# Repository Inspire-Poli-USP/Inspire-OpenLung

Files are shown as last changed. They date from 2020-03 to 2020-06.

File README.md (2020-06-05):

# Inspire-OpenLung

<p align="center">
<a href="https://github.com/Inspire-Poli-USP/Inspire-OpenLung/blob/master/LICENSE" alt="License CERN Open Hardware V2">
        </a>

<a href="https://t.me/openlungpoliusp" alt="Chat em grupo no Telegram">
        </a>

<a href="https://groups.google.com/forum/#!forum/inspireopenlung" alt="Lista de email">
        </a>

<a href="https://inspire-poli-usp.github.io/Inspire-OpenLung/" alt="Docs website">
        </a>
</p>

Seja muito bem vindo ao repositório do projeto de hardware livre OpenLung! Um respirador emergencial brasileiro para enfrentamento da COVID-19!

Um projeto da iniciativa [Inspire Poli-USP](https://www.poli.usp.br/inspire), uma de oito iniciativas da Universidade de São Paulo envolvendo viabilização de respiradores para enfrentamento à pandemia. Para saber mais sobre essa e outras iniciativas [veja esse link](https://prp.usp.br/usp-e-covid-19/).

Considere também apoiar o financiamento de pesquisas na USP para o combate à COVID-19 [através do programa USP Vida](https://www5.usp.br/uspvida/).

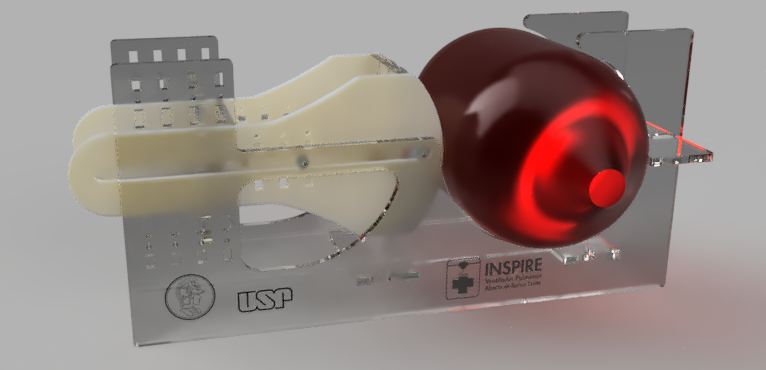
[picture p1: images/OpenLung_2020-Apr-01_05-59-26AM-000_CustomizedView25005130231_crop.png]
Model of CITI-OpenLung


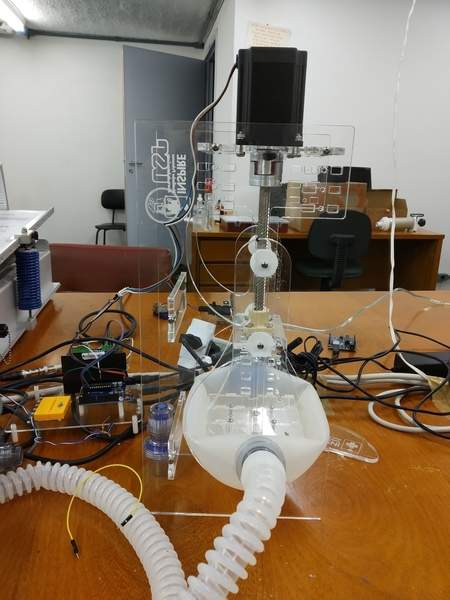
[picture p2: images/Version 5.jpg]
Photo of Prototype Version 5 (https://youtu.be/7Tz8H8FaeOk)


(Clique na imagem acima para ver um vídeo do protótipo em ação)

* * *

## :warning: ATENÇÃO :warning:

-   **Este é um projeto em andamento, não é um produto pronto.**
-   **O projeto em seu atual estado NÃO DEVE SER USADO EM HUMANOS.**
-   **O projeto em seu estado atual NÃO DEVE SER USADO EM ANIMAIS sem aprovação de comitês de ética legítimos.**
-   **Caso futuramente aprovado por autoridades competentes, o projeto NÃO DEVE SER FABRICADO E DISTRIBUÍDO SEM OS CONTROLES DE QUALIDADE necessários para seu uso.**
-   **As entidades e pessoas envolvidas no desenvolvimento desse projeto NÃO SE RESPONSABILIZAM pelo uso de má fé das informações deste projeto ou de projetos derivados deste, que possam por exemplo, mas não limitando-se a, ferir, prejudicar, ludibriar, adoecer, contaminar ou lesar quaisquer pessoas. Caso você julgue ter observado o mau uso deste projeto em quaisquer circunstâncias, nos informe imediatamente pelo contato [inspire@usp.br](mailto:inspire@usp.br) . Sua colaboração é importante para a segurança deste projeto.**
-   **Este projeto usa a licença [CERN-OHL-S 2.0](https://github.com/emersonmoretto/CITI-OpenLung/blob/master/LICENSE).**

* * *

## :exclamation: ATUALIZAÇÃO IMPORTANTE :exclamation:

Devido a questões jurídicas, o entendimento dos coordenadores do projeto é de que o software que realiza o controle do Ambu, bem como os dados experimentais associados aos testes dos algoritmos de controle, permanecerão **privados** até o término dos testes.

Lamentamos essas medidas e estamos discutindo a **possibilidade** do compartilhamento restrito dessas informações com grupos de contribuidores especiais (como centros de pesquisa, universidades, empresas etc) interessados em contribuir com o projeto. Mas isso ainda não está decidido.

Existem [outros repositórios](https://github.com/Inspire-Poli-USP/Inspire-OpenLung/wiki/Outros-Projetos) **independentes da iniciativa Inspire** que estão desenvolvendo, disponibilizando ou prometem disponibilização de firmwares, como por exemplo o [OdaMV](https://github.com/eduoda/odamv), o [ReesistenciaTeam](https://gitlab.com/reesistencia/reespirator/-/tree/dev/rees_firmware), o [hitecnologia/cov19](https://github.com/hitecnologia/cov19) ou o [BMV OpenLung](https://gitlab.com/open-source-ventilator/ventilator/OpenLung/-/tree/master/) - bem como [essa lista de projetos](https://soptechint.com/ventilators). Contudo não nos responsabilizamos pelo uso destes firmwares com nosso hardware e reforçamos a atenção para os [importantes avisos no início desta página](#warning-atenção-warning).

Caso tenha alguma dúvida, pedido ou reclamação, entre em contato com [inspire@usp.br](mailto:inspire@usp.br).

Vale notar que, desde o dia 14 de Abril, o projeto não recebe atualizações em relação ao respirador. Portanto, o que se encontra nesse repositório é tudo que foi feito até essa data e não incorre em problemas jurídicos para equipe do Inspire. Você pode acompanhar as últimas atualizações através dos [Vídeos Relatórios](https://github.com/Inspire-Poli-USP/Inspire-OpenLung/blob/master/LICENSE) e das [Aparições na mídia](https://github.com/Inspire-Poli-USP/Inspire-OpenLung/wiki/Apari%C3%A7%C3%B5es-na-m%C3%ADdia)

* * *

# Índice

| [Nossa Wiki](https://github.com/Inspire-Poli-USP/Inspire-OpenLung/wiki) | [Issues do Projeto](https://github.com/Inspire-Poli-USP/Inspire-OpenLung/issues) | [Pull-Requests](https://github.com/Inspire-Poli-USP/Inspire-OpenLung/pulls) | [Licença de Uso](https://github.com/Inspire-Poli-USP/Inspire-OpenLung/blob/master/LICENSE) |
| ----------------------------------------------------------------------- | -------------------------------------------------------------------------------- | --------------------------------------------------------------------------- | --------------------------------------------------------------------------------------------- |

1.  [Porque mais um projeto como esse?](#porque-mais-um-projeto-como-esse)
2.  [Motivação](#motivação)
3.  [Onde queremos chegar](#onde-queremos-chegar)
4.  [Questão Regulatória](#questão-regulatória)
5.  [Como colaborar](#como-colaborar)
6.  [Nossa Abordagem de Trabalho e Princícios de Design](#nossa-abordagem-de-trabalho-e-princípios-de-design)
7.  [Andamento do projeto](#andamento-do-projeto)</br>
    7.1 [Tarefas pendentes](#tarefas-pendentes)
8.  [Principais Especificações Desejadas](#principais-especificações-desejadas)
9.  [Lista de Materiais](#lista-de-materiais)</br>
    9.1 [Partes Mecânicas](#partes-mecânicas)</br>
    9.2 [Partes Eletrônicas](#partes-eletrônicas)</br>
    9.3 [Partes "Médicas"](#partes-médicas)
10. [Contato e Ajuda](#contato-e-ajuda)
11. [Doe para o projeto](#doe-para-o-projeto)
12. [Licença](#licença)

# Por que mais um projeto como esse

Este é mais um projeto de design de ventilador pulmonar de acesso aberto com o intuito de ser barato, de fácil transporte e utilizando poucos materiais, usando principalmente um Ambu como gerador de fluxo de ar.

Iniciamos este projeto porque até então haviam apenas propostas online com conteúdo parcialmente disponível, e apenas levando em consideração o contexto dos países em que tais propostas estavam/estão sendo desenvolvidas. Nosso projeto se baseia em [Princípios](https://github.com/Inspire-Poli-USP/Inspire-OpenLung/blob/master/Principios_e_abordagem.md) que colocam um peso maior na indisponibilidade de recursos e custo.

Vale notar também que o ventilador pulmonar inspire utiliza em sua maioria produtos que podem ser encontrados com realativa facilidade no mercado Brasileiro.

# Motivação

A expectativa é que teremos no Brasil um pico de casos a serem tratados pelo sistema de saúde pelo final do mês de Abril. Nesse momento a demanda por ventiladores pulmonares mecânicos será crítica, sendo uma das lamentáveis causas de morte pelo novo coronavirus devido a ausência de infraestrutura suficiente para a quantidade de número de pacientes. Estamos lutando contra o tempo para desenvolver um ventilador "open source" que possa ser fabricado antes que isso aconteça.

# Onde queremos chegar

A ideia final é reproduzir um respirador profissional para terapia intensiva. Ou seja:

-   Não é um projeto que se restringe a apenas apertar o Ambú ritmicamente,
-   É um projeto para reproduzir uma curva de variação de pressão definida pelo usuário (médico ou fisioterapeuta),
-   Não queremos fazer um respirador igualmente sofisticado aos comercialmente disponíveis,
-   É um projeto para ter o mínimo necessário para manter pessoas vivas com segurança, [numa situação emergencial](#warning-atenção-warning).

Veja a página ["Entenda o Problema"](https://github.com/Inspire-Poli-USP/Inspire-OpenLung/wiki/Entenda-o-Problema) para informações mais específicas sobre o escopo técnico deste projeto.

Onde queremos chegar com este braço open source da iniciativa Inspire é desenvolver os módulos centrais do ventilador, que identificamos como sendo:

-   o "apertador de Ambu",
-   e o algoritmo de controle.

Os demais módulos como eletrônica própria (sem usar arduino), interface operador-máquina e _packaging_ do sistema todo **por enquanto** não são open source. O firmware e softwares associados ao algoritmo de controle **serão compartilhados de maneira restrita** com contribuidores especiais, pelas razões explicitadas [aqui](#exclamation-atualização-importante-exclamation).

Contudo, você pode desenvolver esses outros módulos segundo seu próprio contexto local de logística e recursos. Uma produção deslocalizada e flexível é uma possibilidade em aberto para fabricação dos respiradores a tempo. Encorajamos possíveis colaboradores deste projeto a seguir o exemplo de forks desre repositório e desenvolverem suas próprias soluções complementares ao que estamos fazendo.

# Questão regulatória

Uma questão em aberto para todos os projetos open source de ventiladores para suporte no combate à COVID-19 é se esses projetos terão aprovação regulatória para serem usados em pacientes.

A expectativa é que em algum momento esse processo se torne mais facilitado por alguma ação do governo e agências reguladoras.

Para saber mais a respeito das informações que temos a respeito dessa atual situação, dê uma olhada na [página da wiki](https://github.com/Inspire-Poli-USP/Inspire-OpenLung/wiki/Regulamenta%C3%A7%C3%A3o) sobre este assunto ou na conversa do [Issue #14](https://github.com/Inspire-Poli-USP/Inspire-OpenLung/issues/14).

# Como Colaborar

Veja nosso [guia de como colaborar](https://github.com/Inspire-Poli-USP/Inspire-OpenLung/blob/master/CONTRIBUTING.md). Nele deixamos claro o que é necessário para o projeto e de que maneira precisamos que você nos ajude. Presumimos que você pode colaborar de maneira autônoma, sem depender de nós - mas apoiamos fortemente interagir conosco e outras pessoas desenvolvendo esse mesmo projeto.

Caso nosso guia não seja o suficiente, você pode saber mais sobre quais são os debates do momento da comunidade entrando no [chat em grupo no Telegram](https://t.me/openlungpoliusp) e vendo a [nossa lista de emails](https://groups.google.com/forum/#!forum/inspireopenlung).

Vale dar uma olhada também no nosso [Código de Conduta](https://github.com/Inspire-Poli-USP/Inspire-OpenLung/blob/master/CODE_OF_CONDUCT.md) para colaboração no projeto deste repositório.

# Nossa Abordagem de Trabalho e Princípios de Design

Acreditamos que toda as tentativas de designs possíveis de respiradoras são válidas por aumentarem as possibilidades de sucesso de ALGUM protótipo de respirador funcionar com qualidade ([veja essa lista detalhada](https://soptechint.com/ventilators) de alguns projetos) e chegar até quem precisa. Na nossa tentativa em particular, [definirmos alguns Princípios fundamentais de Design e nossa Abordagem de Trabalho](https://github.com/Inspire-Poli-USP/Inspire-OpenLung/blob/master/Principios_e_abordagem.md) no desenvolvimento e teste deste protótipo.

Se você se identifica com essa abordagem, considere [colaborar com o projeto](https://github.com/Inspire-Poli-USP/Inspire-OpenLung/blob/master/CONTRIBUTING.md).

Se você gostaria de contribuir usando uma abordagem de trabalho ou princípios diferentes destes, o encorajamos fortemente a desenvolver seu próprio repositório com sua nova proposta - colocando também a mão na massa!

# Andamento do Projeto

Estamos documentando as informações do andamento do projeto principalmente na nossa [Wiki](https://github.com/Inspire-Poli-USP/Inspire-OpenLung/wiki).

Essa é uma resumida linha do tempo do projeto:

-   20 de Março: Início do Projeto
-   21 de Março: Modelagem 3D do Design e Fabricação do Protótipo V1
-   22 de Março: Testes do V1. Modelagem e Fabricação do Protótipo V2.2: ampliando posibilidades de posicionamento do motor e fuso trapezoidal.
-   23 de Março: Testes na versao 2.2 com um equipamento que mede volume, pressão e velocidade, obtivemos:
      27 ciclos por minuto
      250 mL de volume (este valor precisa alcancar 600 mL)
      30 cm H2O de pressão
      Conclusão: trocar o motor para NEMA 23 15kg de torque e usar um fuso de avanço maior.
-   24 de Março: Modelagem 3D e testes do Protótipo V3: agora projetado para motor NEMA 23 de 15kg de torque
-   25 de Março: Modelagem 3D e testes do Protótipo V4: Ajustes para diminuir atrito e ser mais resistente a torção
-   26 de Março: Primeira versão, ainda incompleta, do firmware
-   27 de Março: Desenvolvendo o firmware para primeiros testes usando sensor de pressão para controle
-   29 de Março: Implementação do controlador PID
-   30 de Março: Implementação e testes do firmware com controlador PID duplo (Gain Scheduling)
-   31 de Março: Versão 5, com ajustes para atingir uma maior área do ambú
-   1 de Abril a 12 de Abril: Implementações e testes de diferentes algoritmos de controle e testes de capacidade em diferentes cenários reais.
-   13 de Abril a 16 de Abil: [Testes em animais](https://www1.folha.uol.com.br/colunas/monicabergamo/2020/04/ventilador-da-poli-sera-testado-em-animais-e-pessoas-e-pode-ser-lancado-em-uma-semana.shtml)

Vale notar que essa linha do tempo não é atualizada desde 14 de abril. Você pode acompanhar as últimas atualizações através dos [Vídeos Relatórios](https://github.com/Inspire-Poli-USP/Inspire-OpenLung/blob/master/LICENSE) e das [Aparições na mídia](https://github.com/Inspire-Poli-USP/Inspire-OpenLung/wiki/Apari%C3%A7%C3%B5es-na-m%C3%ADdia).

## Tarefas Pendentes

-   Testes em Humanos (devidamente regularizado e aprovado por comitês de ética competentes)

Dê também uma olhada nos nossos [Issues](https://github.com/Inspire-Poli-USP/Inspire-OpenLung/issues) e [Pull-Requests](https://github.com/Inspire-Poli-USP/Inspire-OpenLung/pulls).

# Principais Especificações Desejadas

-   Ser robusto. Deve funcionar continuamente sem falhas (ciclo de trabalho de 100%) por períodos de 14 dias, 24 horas por dia. Se necessário, a máquina pode ser substituída depois de cada período de 14 dias de uso ininterrupto.

-   Prover ao mínimo duas possibilidades de configuração de volume de mistura de ar/O2 entregues por ciclos de respiração. Essas possibilidades devem ser 450ml +/- 10ml por respiração and 350ml +/- 10ml por respiração.

-   Prover essa mistura de ar/Oxigêno a até um pico de 350 mm de H2O.

-   Ter a capacidade de adaptação aos materiais de tubagem, mantendo o paciente pressurizado a todo momento a 150 mm H2O.

-   Ser ajustável para uma taxa de 12 a 20 ciclos/respirações por minuto.

-   Entregar no mínimo 400 mL de mistura de ar/Oxigênio em não mais que 1,5 segundo. A funcionalidade de mudança dessa velocidade em que o ar é empurrado dentro do paciente é desejável, mas não essencial.

# Lista de Materiais

## Partes Mecânicas

-   Acoplador de Garra Drylin E para eixo redondo de 10 mm de diâmetro
-   Fuso Trapezoidal de 10 mm de diâmetro, 15 cm de comprimento e passo de 25 mm
-   Castanha de Latão TR10 e passo de 2,5 mm
-   20x parafusos M3 de 16mm de comprimento
-   20x porcas M3
-   4x parafusos M4 de 16mm de comprimento
-   Chapa de acrílico de 5mm com no máximo 76 cm x 40 cm
    -   Resulta em **apenas 12 peças**:
        -   2x "Suporte de Pistão" (V5)
        -   2x "Pistões" (V5)
        -   2x "Ponta do Pistão" (V5)
        -   1x "Chapa do Motor" (V5)
        -   1x "Chapa da Castanha" (V5)
        -   1x "Chapa do Pistão" (V5)
        -   1x "Suporte do Ambu" V5
        -   2x "Conector Inferior" (V5)

## Partes Eletrônicas

-   1x Nema 23 15kg
-   1x Arduino uno
-   1x Driver DW322E da Leadshine
-   Fonte de 12v 5A
-   4x jumpers macho-macho

## Partes "Médicas"

-   1x Ambu com capacidade de 1600 mL
-   2x Tubo traqueia de 1 m
-   1x Válvula unidirecional de CPAP com acoplamento para válvula PEEP
-   1x Válvula PEEP com ajuste de 5 a 15 cmH2O

_(OBS: as "Partes Médicas" podem variar de nome em cada região; outros produtos médicos de finalidade semelhante podem ser usados)_

# Contato e Ajuda

Se as informações aqui ainda não forem exatamente o que você está procurando, preencha [esse formulário rápido](https://forms.gle/2u1fxgFx3JDqjxeX7) que falaremos com você assim que possível!

# Doe para o projeto

Caso você queira demonstrar seu suporte ao projeto, você tem a opção de doar para a iniciativa Inspire, através do [link](
https://www.vakinha.com.br/vaquinha/inspire-respirador-da-escola-politecnica-da-usp-fase-2 ). Toda doação é bem vinda.

Caso não possa doar, não tem problema. Você também pode demonstrar suporte ao projeto colocando uma ⭐️ nesse repositório. Obrigado!

# Licença

[CERN Open Hardware V2](https://github.com/Inspire-Poli-USP/Inspire-OpenLung/blob/master/LICENSE)

**Obrigado por visitar nosso repositório e se interessar pelo projeto!**

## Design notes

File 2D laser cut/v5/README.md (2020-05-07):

# Release V5

## emoretto @ 01/04/2020 2:20AM

-   Maior área de ataque ao ambú (30% maior), com o objetivo de ganhar um pouco mais de volume com o mesmo curso do pistao/motor

-   Adição de 2 plates pra ataque ao ambú com o objetivo de entrar mais uniforme

-   Plate de suporte do ambu está otimizado para permitir que o ventilador possa ficar na posição vertical

-   Novos furos no pistao para permitir o uso de fuso menor (130mm mínimo)

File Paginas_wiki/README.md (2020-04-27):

# Páginas da Wiki

Este repositório possui uma [Wiki](https://github.com/Inspire-Poli-USP/Inspire-OpenLung/wiki). Nela, além de relatórios das nossas atividade, é o local de conteúdos explicativos, tutoriais, informações, recursos gerais e etc.

As páginas da Wiki devem ter arquivos redundantes em markdown nesta pasta. Fazemos isso como medida de melhorar a contribuição da comunidade com informações úteis na Wiki, usando o próprio sistema de versionamento git deste repositório.

Após editar ou criar quaisquer arquivos nesta pasta, analisaremos o pull-request e logo após o merge copiaremos o conteúdo na respectiva página na [Wiki](https://github.com/Inspire-Poli-USP/Inspire-OpenLung/wiki).

Caso isso não aconteça ou para qualquer outro problema identificado, por favor, crie um [Issue](https://github.com/Inspire-Poli-USP/Inspire-OpenLung/issues) sobre o assunto.

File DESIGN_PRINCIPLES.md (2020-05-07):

# Princípios de Design do Projeto

Este projeto segue uma abordagem com os seguintes pontos fundamentais e suas justificativas:

1.  Peças fabricáveis apenas por corte a laser
    -   Processos de prototipagem e de produção industrial muito semelhantes
        -   Facilidade de passagem do protótipo para o processo industrial
        -   Mais simples do que impressão 3D, que precisaria da fabricação de moldes de injeção específicos, por exemplo.
    -   Facilidade de uso de diferentes materiais para o mesmo design e processo de fabricação
        -   Ex: corte de chapas de acrílico no protótipo mas podendo ser chapas de alumínio no produto industrial
    -   Velocidade de fabricação maior que impressão 3D
2.  Poucas peças
    -   Facilidade de montagem
    -   Rapidez de montagem
    -   Menor custo
    -   Menor complexidade
        -   Menor probabilidade de erros de projeto
        -   Menor probabilidade de erros de montagem
3.  Uso de tubulações, válvulas passivas e compartimentos de Ar já usados em aplicações médicas
    -   Funcionalidade já validada
    -   Uso regulamentado
    -   Familiaridade com os profissionais de saúde
    -   Diminuição do escopo de desenvolvimento do projeto
        -   Projeto menos complexo
        -   Projeto mais ágil
4.  Uso de motor de passo
    -   Capacidade de controle de movimento preciso
        -   Possibilita controle preciso da curva de respiração **apenas** com o pressionamento de compartimento flexível contendo Ar e/ou Oxigênio
5.  Poucos componentes móveis
    -   Facilidade de montagem
    -   Rapidez de montagem
    -   Menor custo
    -   Menor complexidade
        -   Menor probabilidade de erros de projeto
        -   Menor probabilidade de erros de montagem
6.  Movimento de compressão unidirecional e ortogonal ao compartimento flexível de compressão
    -   Permite a flexibilidade de adoção (caso eventualmente necessário) de diferentes compartimentos (Ambu, sanfona etc) usando essencialmente o mesmo design
7.  Ausência de válvulas de controle de pressão/vazão da mistura Ar/O2 que vai ao paciente
    -   Menor custo
    -   Menor complexidade
    -   Menor dependência de peças de terceiros
8.  Ausência de monitoramento de % de O2
    -   Menor custo
    -   Ajuste da % de O2 aproveitando o manômetro do cilindro de O2
        -   Pré-calibração da mistura de Ar/O2 por ajuste do manômetro é robusta
        -   Mistura de Ar e O2 aproveitando o compartimento flexível de compressão (ex: Ambu)

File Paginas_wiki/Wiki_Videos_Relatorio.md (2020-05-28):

Abaixo estão todos os vídeos relatório gravados, em ordem cronológica. Todos os vídeos podem ser encontrados no [Canal do YouTube da POLI-USP](https://www.youtube.com/channel/UCJU4uI6j2lfSKkzktwFWQRw). Os interlocutores dos vídeos normalmente são o professor Marcelo Zuffo e o professor Raúl Lima.

# 1 de Abril

Apresentação inicial do INSPIRE, o ventilador pulmonar aberto da USP.

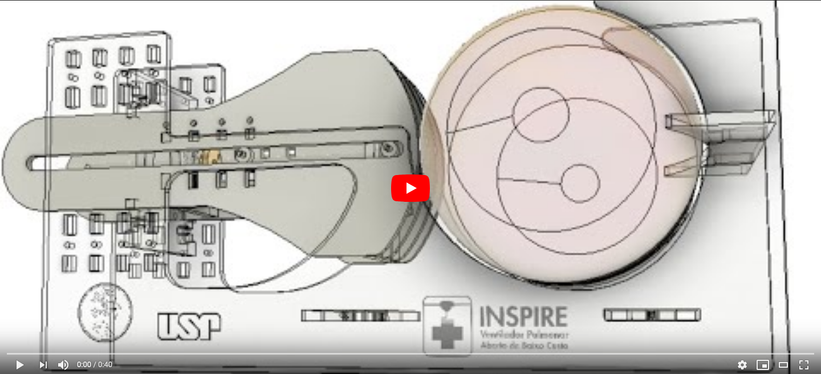
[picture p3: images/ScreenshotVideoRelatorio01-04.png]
Vídeo relatório 1 de Abril (https://www.youtube.com/watch?v=ApoKv4ukpX4&)


# 2 de Abril

Comentários sobre o trabalho desenvolvido no dia 2 de Abril. Foi apresentado o trabalho desenvolvido pelo Felipe, que foram estimativas da complacência e da resistência do pulmão.

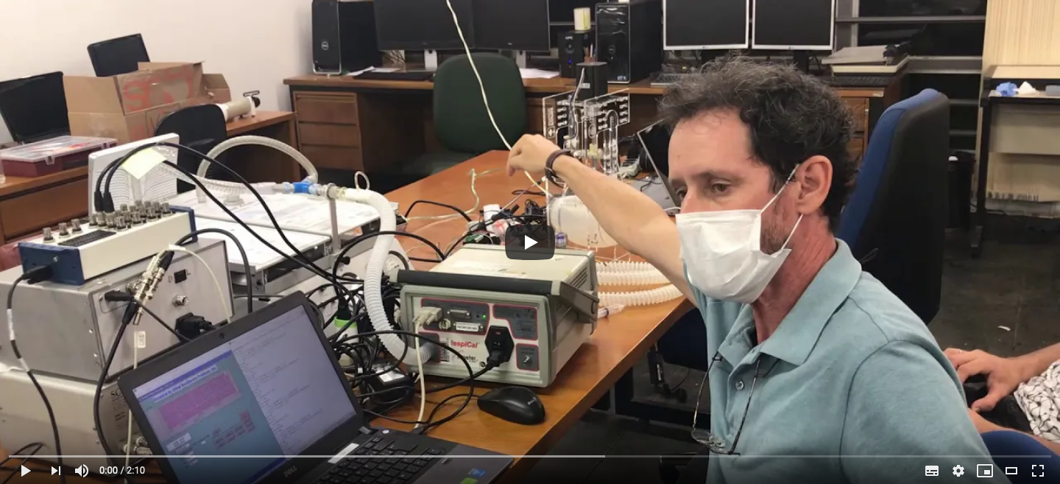
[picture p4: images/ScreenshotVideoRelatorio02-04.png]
Vídeo relatório 2 de Abril (https://www.youtube.com/watch?v=P73DMeOfYrI&)


# 6 de Abril

Comentários sobre o algorítmo de controle utilizado no INSPIRE.

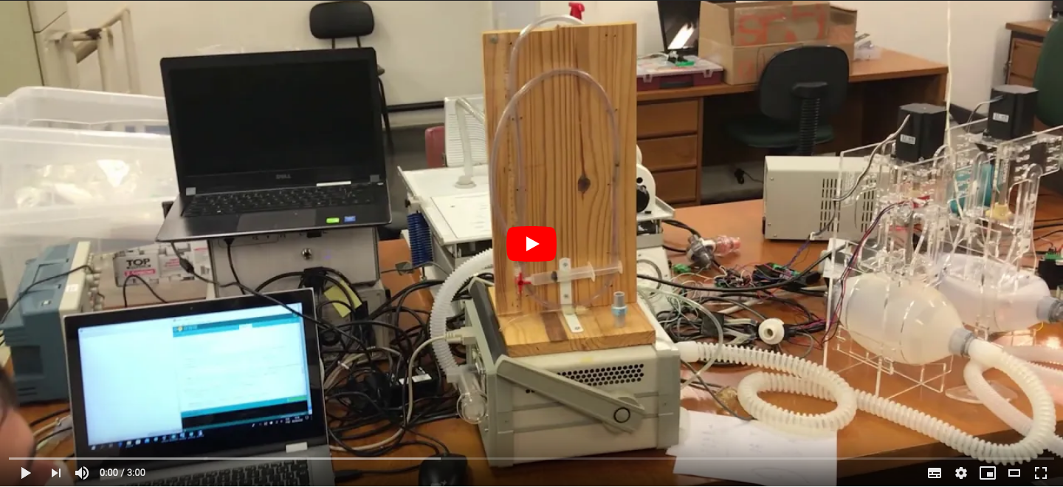
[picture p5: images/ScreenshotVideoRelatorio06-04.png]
Vídeo relatório 6 de Abril (https://www.youtube.com/watch?v=ZsHDVqar_dg&)


# 8 de Abril - Avaliação do projeto de ventilador pulmonar do MIT

Avaliação de uma réplica modificada do ventilador pulmonar do MIT. Foram mostradas sugestões de mudanças para o projeto.

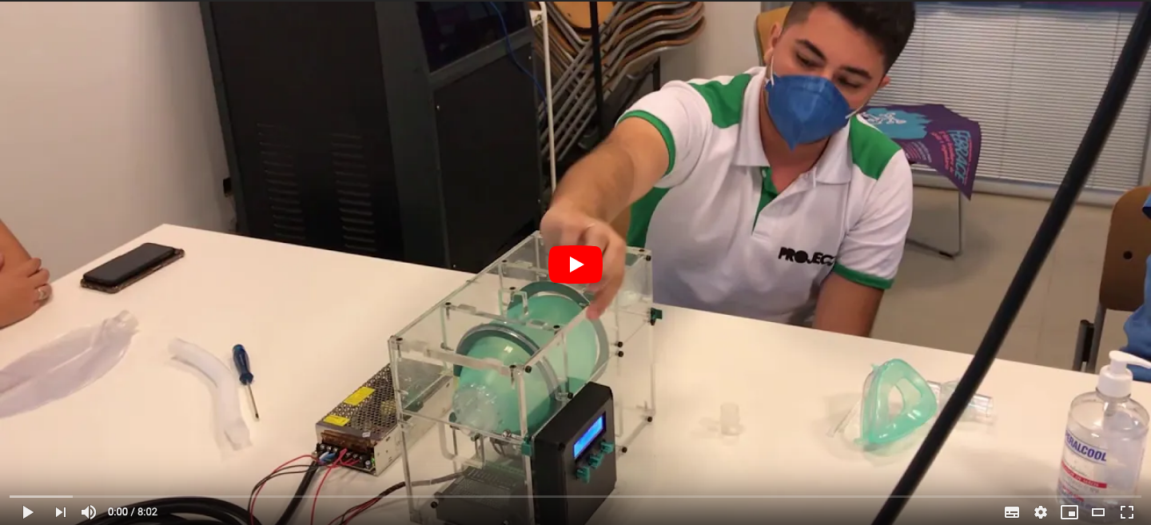
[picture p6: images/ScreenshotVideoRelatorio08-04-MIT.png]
Vídeo relatório 8 de Abril - Avaliação do projeto de ventilador pulmonar do MIT (https://www.youtube.com/watch?v=m1voC9npYlY&)


# 8 de Abril

Mostrando avanços, os inspires começaram a ser produzidos. Houve também avanços no algoritmo de controle.

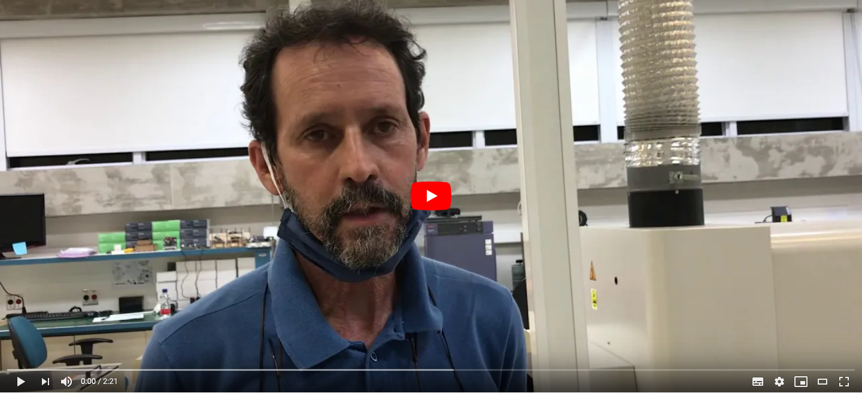
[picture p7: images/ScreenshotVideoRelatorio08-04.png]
Vídeo relatório 8 de Abril (https://www.youtube.com/watch?v=hkaXHtFTmG4&)


# 9 de Abril

Explicação sobre os softwares utilizados no projeto INSPIRE. Foi utilizado o algoritmo PID, bem como outros algoritmos de controle.

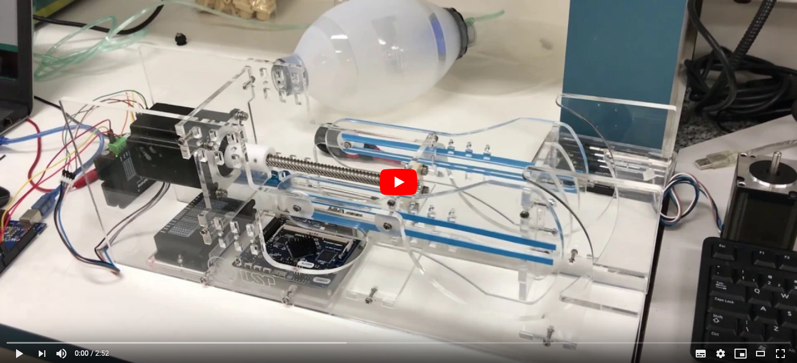
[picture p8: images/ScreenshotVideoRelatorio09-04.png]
Vídeo relatório 9 de Abril (https://www.youtube.com/watch?v=Z26OczABk4o&)


# 11 de Abril

Foram conseguidas melhoras no algoritmo PID. Foi mostrada a última versão do INSPIRE além de comentários sobre a interface gráfica.

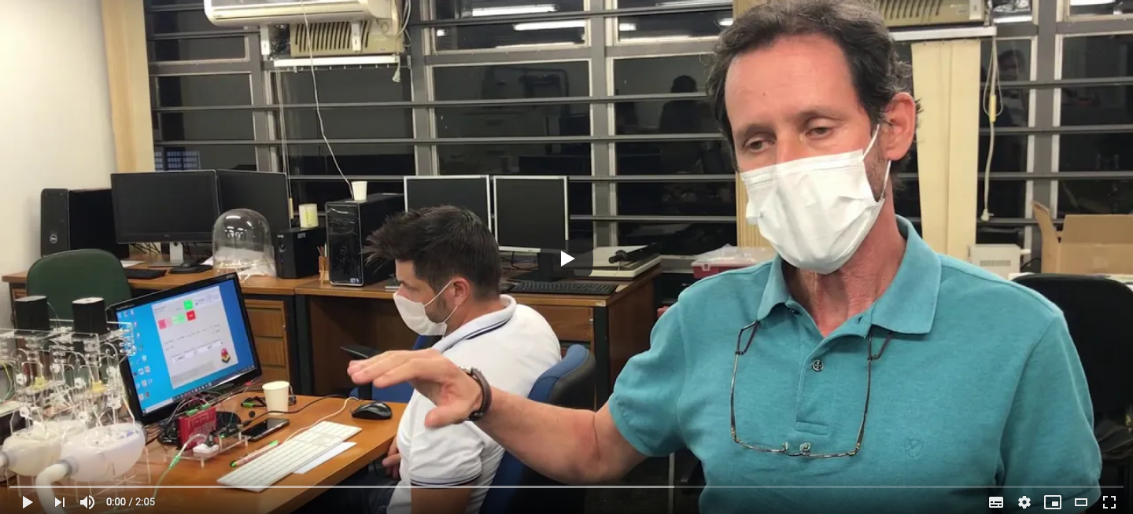
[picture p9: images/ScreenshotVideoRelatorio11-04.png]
Vídeo relatório 11 de Abril (https://www.youtube.com/watch?v=jyhIea9kIBM&)


# 16 de Abril

Foram mostrados testes de integração e a placa da caninos (labrador).

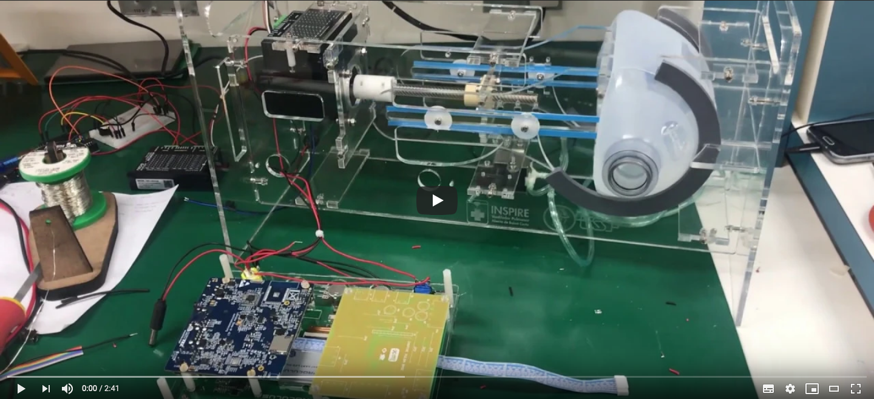
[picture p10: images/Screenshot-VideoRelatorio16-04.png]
Vídeo relatório 16 de Abril (https://www.youtube.com/watch?v=5Bk71natObE&)


# 18 de Abril

Foram mostradas uma tela sensível ao toque juntamente com as placas labrador, pulga e speedbase.

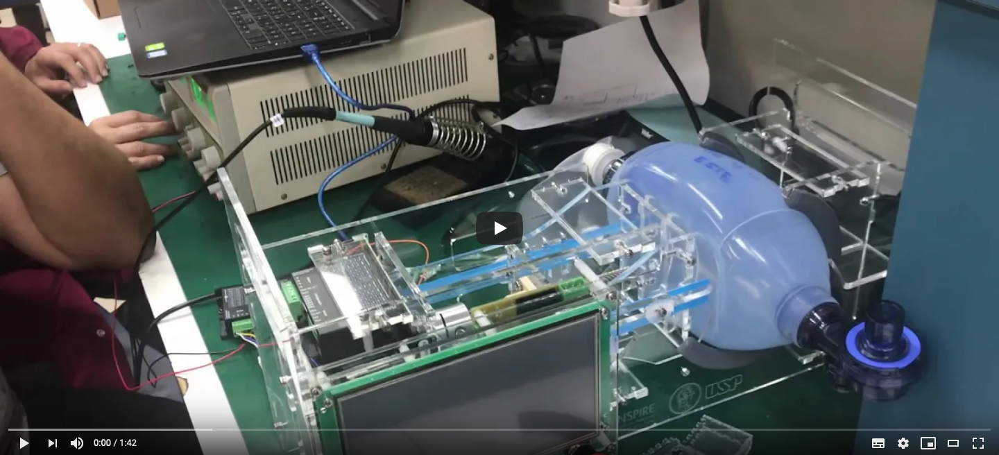
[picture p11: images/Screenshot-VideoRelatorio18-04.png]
Vídeo relatório 18 de Abril (https://www.youtube.com/watch?v=kMW-kKYsIrE&)


# 19 de Abril

Foi mostrado uma versão do inspire com um drive de 24V (DM-542).

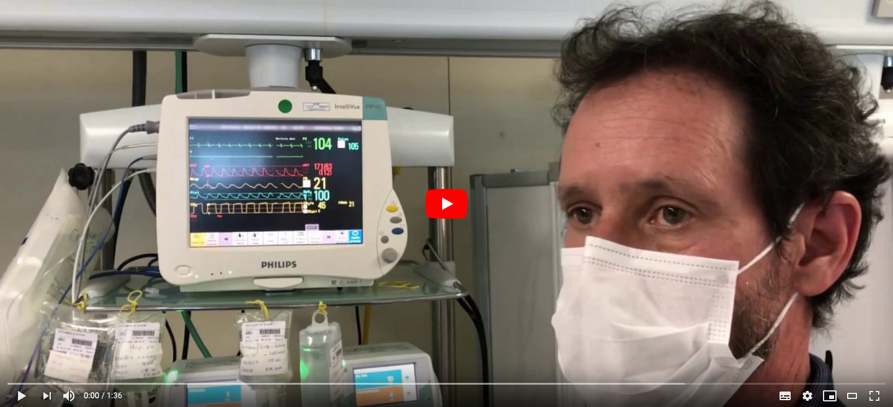
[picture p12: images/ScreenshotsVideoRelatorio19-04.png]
Vídeo relatório 19 de Abril (https://www.youtube.com/watch?v=b0nxfpfzyJo&)


# 24 de Abril

Foi o inspire no Instituto do Coração, onde foram feitos os testes com pacientes.

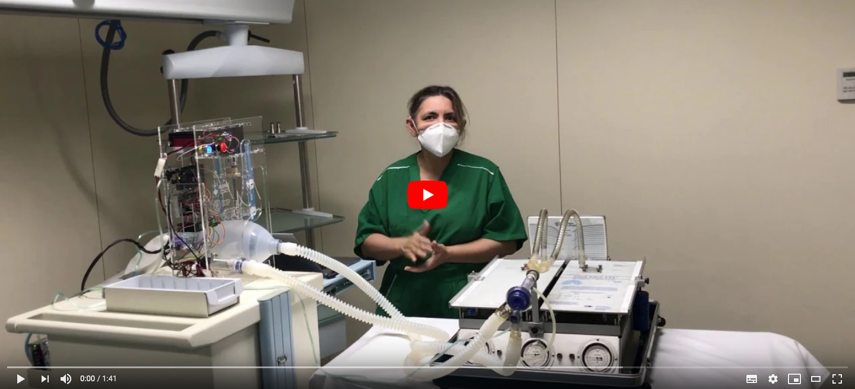
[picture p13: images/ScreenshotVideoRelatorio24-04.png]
Vídeo relatório 24 de Abril (https://www.youtube.com/watch?v=mknScegvswc&)


# 25 de Abril

Foi mostrado a ultima versão do inspire juntamente com membros do IFSP.

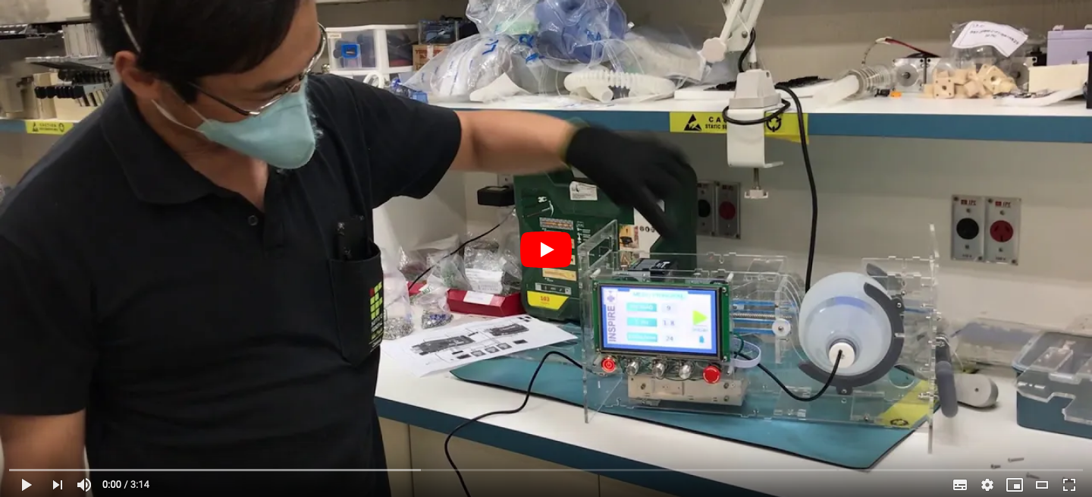
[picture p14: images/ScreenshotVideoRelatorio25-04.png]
Vídeo relatório 25 de Abril (https://www.youtube.com/watch?v=qGx5H0k_fXg&)


# 26 de Abril a 1 de Maio

Foi mostrado o início de uma conversa entre o professor Raúl e a Globo, além dos últimos desenvolvimentos do projeto INSPIRE. Foi também mostrado o capacete de respiração do projeto inspire em testes.

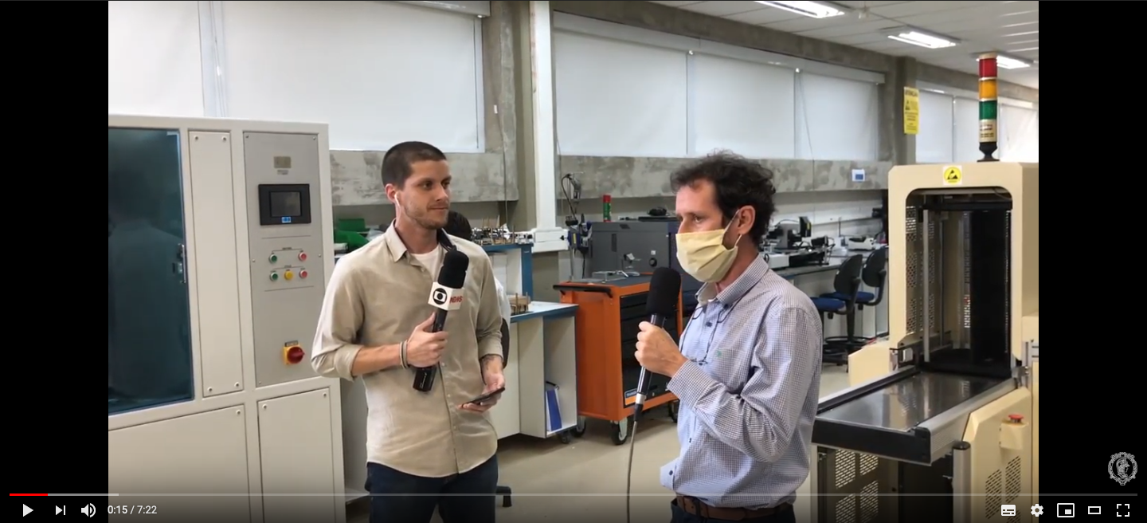
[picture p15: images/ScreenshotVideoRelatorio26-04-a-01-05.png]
Vídeo relatório 26 de Abril a 1 de Maio (https://www.youtube.com/watch?v=pATzXCSPYv0&)


# 7 de Maio

Apresentação da última versão disponível do projeto INSPIRE, além de uma demonstração de seu funcionamento em um pulmão artificial.

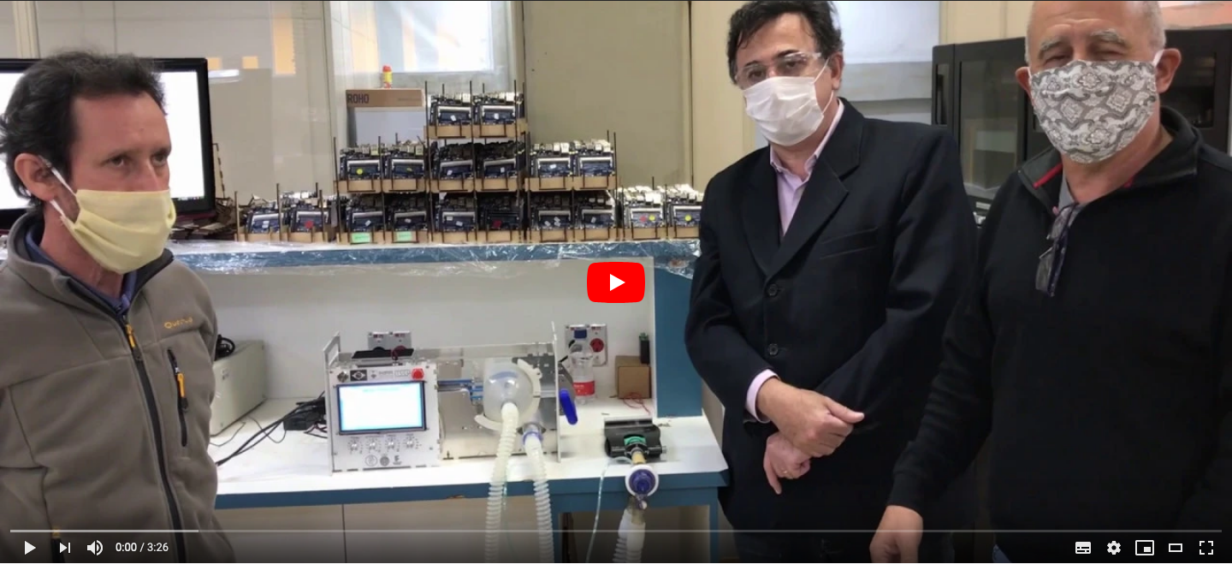
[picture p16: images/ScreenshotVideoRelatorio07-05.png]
Vídeo relatório 7 de Maio (https://www.youtube.com/watch?v=RuhyQjUJICo&)


# 7 de Maio - agradecimento a Mapfre

Vídeo em agradecimento a fundação Mapfre.

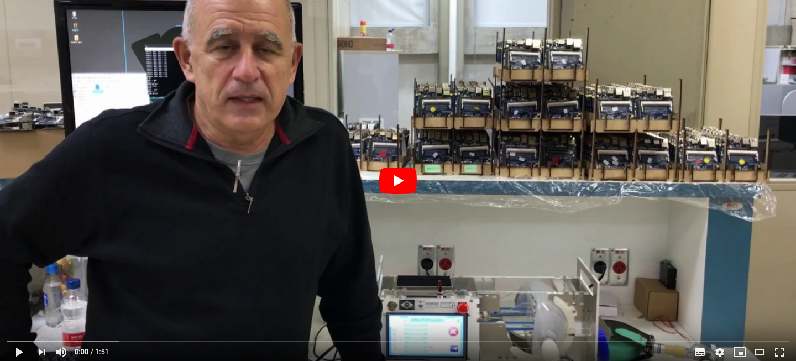
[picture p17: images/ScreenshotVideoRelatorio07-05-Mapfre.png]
Vídeo relatório 7 de Maio - agradecimento a Mapfre (https://www.youtube.com/watch?v=c5Oz3sfg-Bc&)


# 11 de Maio

Mostrando a montagem de placas

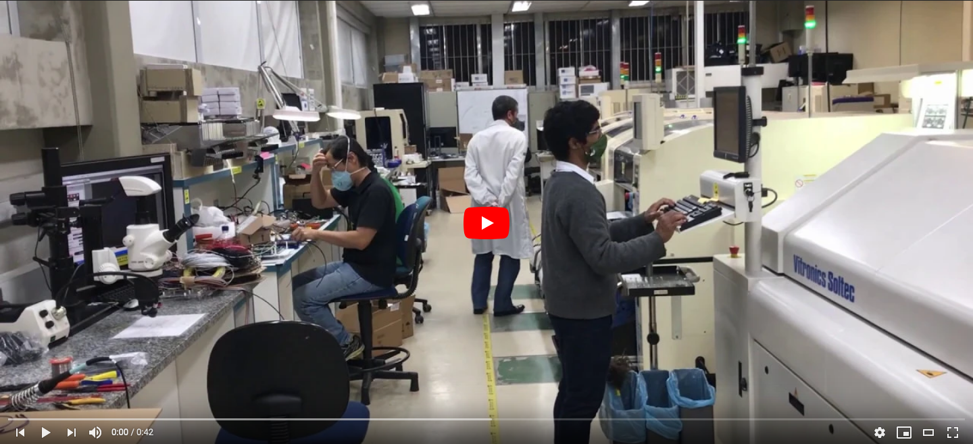
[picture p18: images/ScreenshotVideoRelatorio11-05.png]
Vídeo relatório 11 de Maio (https://www.youtube.com/watch?v=nM5DBFZ39Sc&)


# 16 de Maio

Mostrando a montagem dos respiradores

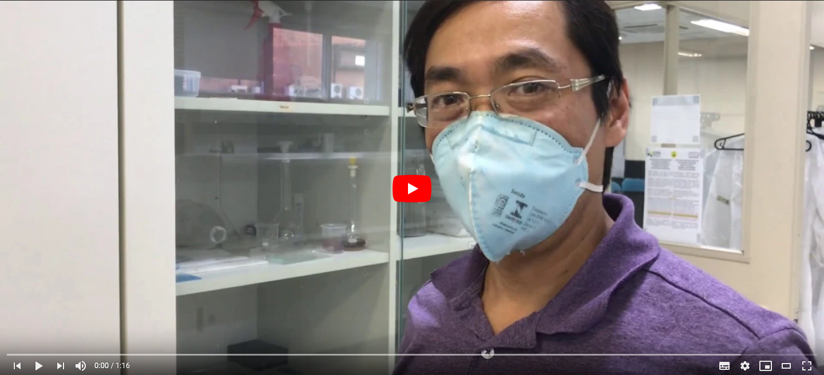
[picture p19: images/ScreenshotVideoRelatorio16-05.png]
Vídeo relatório 16 de Maio (https://www.youtube.com/watch?v=zLtI14aLwO0&)


# 17 de Maio

Teste conceitual para alimentar o inspire com baterias externas

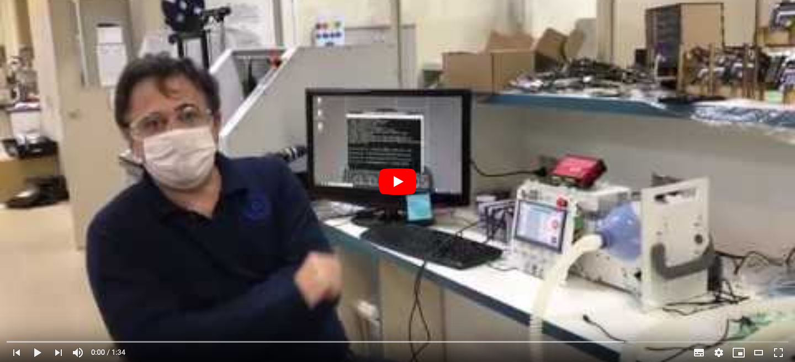
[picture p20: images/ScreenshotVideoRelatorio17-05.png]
Vídeo relatório 17 de Maio (https://www.youtube.com/watch?v=GDAn07QxqBs&)


# 20 de Maio

Apresentação do ventilador pulmar inspire, versão 1.0, revisão A. É demonstrado os respectivos alarmes sendo disparados, como requerido pela Anvisa.

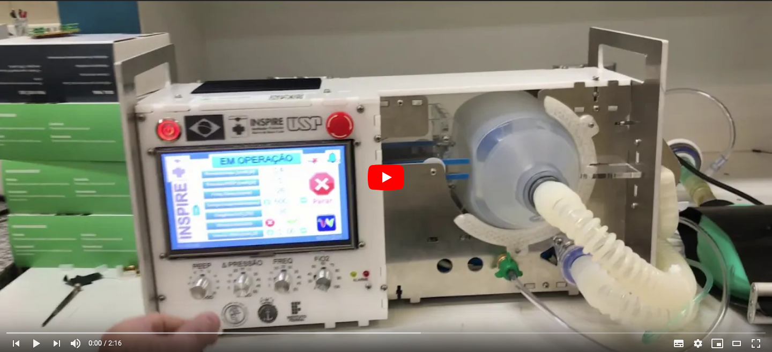
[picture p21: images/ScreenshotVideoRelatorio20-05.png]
Vídeo relatório 20 de Maio (https://www.youtube.com/watch?v=67cH9n0KaH0&)


# 23 de Maio

Apresentação do time do Inspire, demonstrando o funcionamento do respirador. É também notado que a maioria das peças usadas no Inspire podem ser obtidas no mercado nacional.

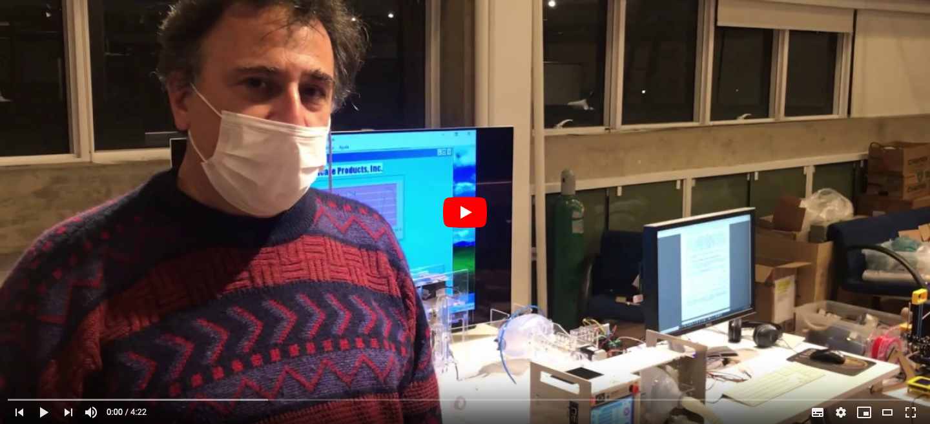
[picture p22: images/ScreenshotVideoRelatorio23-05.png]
Vídeo relatório 23 de Maio (https://www.youtube.com/watch?v=zmSFLScwdpU&)


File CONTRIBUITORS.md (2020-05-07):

# Contribuidores do Projeto - Incluido aqueles não mostrados pelo Git

-   **[Otto Heringer](https://github.com/OttoHeringer)**

-   **[Breno Helfstein Moura](https://github.com/breno-helf/)**

    -   Organização do repositório e explicações de git para organizadores

-   **[Emerson Moretto](https://github.com/emersonmoretto)**

-   **[Matheus Tavares](https://github.com/matheustavares)**

-   **[Wendell Pereira da Silva](https://github.com/silvawp)**

-   **[João Antônio Cardoso](https://github.com/joaoantoniocardoso)**

-   **Marcelo Knörich Zuffo**

    -   Coordenador do projeto

-   **Raúl gonzalez lima**

    -   Coordenador do projeto

-   **Alembert eistein lino alvarado**

    -   Equipe Técnica

-   **Dario GramorellI**

    -   Equipe Técnica

-   **Felipe Fava de Lima**

    -   Equipe Técnica

-   **Francisco Baccaro Nigro**

    -   Equipe Técnica

-   **Henrique Takachi Moriya**

    -   Equipe Técnica

-   **Silvio Andrade Figueiredo**

    -   Equipe Técnica

-   **Renato de Lima Vitorasso**

    -   Equipe Técnica

**[Lista de contribuidores com conta no github atualizada](https://github.com/Inspire-Poli-USP/Inspire-OpenLung/graphs/contributors).**

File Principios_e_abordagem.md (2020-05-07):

# Abordagem de Trabalho

Para entender melhor como estamos fazendo esse trabalho, nossa abordagem é:

-   Construir e testar rapidamente
    -   "mais mão-na-massa"
-   Basear decisões de projeto principalmente em dados de testes
    -   "o argumento mais forte é a evidência"
-   Garantir a qualidade do produto final
    -   "feito não é melhor que perfeito... é um equipamento para manter gente viva"
-   Considerar todos os projetos sendo feitos para encurtar trabalho
    -   "o porco do MIT E-VENT ficou vivo?"
    -   "em que pé que está sistema de controle dos espanhóis do 'ReesistenciaTeam'?"
    -   "o pessoal da UFRJ já começou a testar o que eles estão fazendo?"
-   Colaborar rapidamente com desenvolvedores/testadores empenhados em ajudar
    -   "o pessoal de Joinvile está cortando e testando nosso modelo mais rápido que a gente (risos)"

# Princípios de Design do Projeto

Nos baseamos nas seguintes escolhas de design e suas justificativas. Elas são pontos fundamentais que norteiam as tomadas de decisão:

1.  Peças fabricáveis apenas por corte a laser
    -   Processos de prototipagem e de produção industrial muito semelhantes
        -   Facilidade de passagem do protótipo para o processo industrial
        -   Mais simples do que impressão 3D, que precisaria da fabricação de moldes de injeção específicos, por exemplo.
    -   Facilidade de uso de diferentes materiais para o mesmo design e processo de fabricação
        -   Ex: corte de chapas de acrílico no protótipo mas podendo ser chapas de alumínio no produto industrial
    -   Velocidade de fabricação maior que impressão 3D
2.  Poucas peças
    -   Facilidade de montagem
    -   Rapidez de montagem
    -   Menor custo
    -   Menor complexidade
        -   Menor probabilidade de erros de projeto
        -   Menor probabilidade de erros de montagem
3.  Uso de tubulações, válvulas passivas e compartimentos de Ar já usados em aplicações médicas
    -   Funcionalidade já validada
    -   Uso regulamentado
    -   Familiaridade com os profissionais de saúde
    -   Diminuição do escopo de desenvolvimento do projeto
        -   Projeto menos complexo
        -   Projeto mais ágil
4.  Uso de motor de passo
    -   Capacidade de controle de movimento preciso
        -   Possibilita controle preciso da curva de respiração **apenas** com o pressionamento de compartimento flexível contendo Ar e/ou Oxigênio
5.  Poucos componentes móveis
    -   Facilidade de montagem
    -   Rapidez de montagem
    -   Menor custo
    -   Menor complexidade
        -   Menor probabilidade de erros de projeto
        -   Menor probabilidade de erros de montagem
6.  Movimento de compressão unidirecional e ortogonal ao compartimento flexível de compressão
    -   Permite a flexibilidade de adoção (caso eventualmente necessário) de diferentes compartimentos (Ambu, sanfona etc) usando essencialmente o mesmo design
7.  Ausência de válvulas de controle de pressão/vazão da mistura Ar/O2 que vai ao paciente
    -   Menor custo
    -   Menor complexidade
    -   Menor dependência de peças de terceiros
8.  Ausência de monitoramento de % de O2
    -   Menor custo
    -   Ajuste da % de O2 aproveitando o manômetro do cilindro de O2
        -   Pré-calibração da mistura de Ar/O2 por ajuste do manômetro é robusta
        -   Mistura de Ar e O2 aproveitando o compartimento flexível de compressão (ex: Ambu)

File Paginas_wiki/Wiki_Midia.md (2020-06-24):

Abaixo estão algumas das aparições do ventilador pulmonar da USP, o INSPIRE, na mídia. Acreditamos que é importante documentar as aparições na mídia, por ordem cronológica e por jornais, para que se tenha ideia do que é comunicado para a comunidade externa em relação ao projeto.

## Globo G1

- _(31/03/2020)_ [Coronavírus: Pesquisadores da USP criam ventilador pulmonar para emergências feito em 2 horas e 15 vezes mais barato](https://g1.globo.com/sp/sao-paulo/noticia/2020/03/31/coronavirus-pesquisadores-da-usp-criam-ventilador-pulmonar-para-emergencias-feito-em-2-horas-e-15-vezes-mais-barato.ghtml)

- _(02/04/2020)_ [Grande São Paulo tem 98 mil ventiladores mecanicos em uso em quase 450 hospitais](https://g1.globo.com/sp/sao-paulo/noticia/2020/04/02/grande-sao-paulo-tem-98-mil-ventiladores-mecanicos-em-uso-em-quase-450-hospitais.ghtml) - Menção ao INSPIRE no fim da matéria

- _(03/04/2020)_ [Pesquisadores em São Paulo desenvolvem ventiladores pulmonares mecanicos de baixo custo](https://g1.globo.com/jornal-nacional/noticia/2020/04/03/pesquisadores-em-sao-paulo-desenvolvem-ventiladores-pulmonares-mecanicos-de-baixo-custo.ghtml) - Aparição no Jornal Nacional

- _(14/04/2020)_ [Coronavúrus: Pesquisadores da USP testam ventilador pulmonar para emergências e dizem que resultado é promissor](https://g1.globo.com/sp/sao-paulo/noticia/2020/04/14/coronavirus-pesquisadores-da-usp-testam-ventilador-pulmonar-para-emergencias-e-dizem-que-resultado-e-promissor.ghtml)

- _(27/05/2020)_ [Respirador criado na USP é aprovado em testes com humanos; aparelho é feito em 2 horas e 15 vezes mais barato](https://g1.globo.com/sp/sao-paulo/noticia/2020/04/27/respirador-criado-na-usp-e-aprovado-em-testes-com-humanos-aparelho-e-feito-em-2-horas-e-15-vezes-mais-barato.ghtml)

- _(12/05/2020)_ [Ministério Público questiona governo de SP sobre a falta de atenção com projeto da USP que criou respirador de baixo custo](https://g1.globo.com/sp/sao-paulo/noticia/2020/05/12/ministerio-publico-questiona-governo-de-sp-sobre-falta-de-atencao-com-projeto-da-usp-que-criou-respirador-de-baixo-custo.ghtml)

## Jornal da USP

- _(27/03/2020)_ [Projeto da Poli permite construir ventiladores pulmonares mais baratos em tempo recorde](https://jornal.usp.br/ciencias/ciencias-exatas-e-da-terra/projeto-da-poli-permite-construir-ventiladores-pulmonares-90-mais-baratos-em-tempo-recorde/)

- _(17/04/2020)_ [USP contra a covid-19: conheça as várias ações da Universidade para ajudar no combate à pandemia](https://jornal.usp.br/universidade/usp-contra-a-covid-19-conheca-as-varias-acoes-da-universidade-para-ajudar-no-combate-a-pandemia/)

- _(22/04/2020)_ [Ventilador pulmonar emergencial criado por engenheiros da USP é aprovado nos testes](https://jornal.usp.br/ciencias/ventilador-pulmonar-emergencial-criado-por-engenheiros-da-usp-e-aprovado-nos-testes/)

- _(08/05/2020)_ [USP e Marinha do Brasil se preparam para produzir ventiladores pulmonares](https://jornal.usp.br/institucional/usp-e-marinha-do-brasil-se-preparam-para-produzir-ventiladores-pulmonares/)

- _(12/05/2020)_ [Pesquisadores da USP desenvolvem “capacete-respirador” para tratar pacientes com a covid-19](https://jornal.usp.br/ciencias/cientistas-da-usp-desenvolvem-capacete-respirador-para-tratar-pacientes-com-a-covid-19/)

## Record R7

- _(28/03/2020)_ [Pesquisadores da USP criam ventilador pulmonar de baixo custo](https://noticias.r7.com/educacao/pesquisadores-da-usp-criam-ventilador-pulmonar-de-baixo-custo-28032020)

- _(01/04/2020)_ [Pesquisadores da USP criam ventilador pulmonar para covid-19](https://noticias.r7.com/sao-paulo/pesquisadores-da-usp-criam-ventilador-pulmonar-para-covid-19-01042020)

- _(11/05/2020)_ [Respirador de baixo custo fabricado em 2h entra em fase final de testes](https://noticias.r7.com/saude/respirador-de-baixo-custo-fabricado-em-2h-entra-em-fase-final-de-testes-11052020)

- _(13/05/2020)_ [USP cria 'capacete respirador' para tratar paciente com covid-19](https://noticias.r7.com/tecnologia-e-ciencia/usp-cria-capacete-respirador-para-tratar-paciente-com-covid-19-13052020)

## UOL e Folha de São Paulo

- _(20/04/2020)_ [Ventilador pulmonar da USP já pode entrar na linha de produção](https://www1.folha.uol.com.br/equilibrioesaude/2020/04/ventilador-pulmonar-da-usp-ja-pode-entrar-na-linha-de-producao.shtml)

- _(27/04/2020)_ [Respirador de baixo custo criado pela USP é aprovado em testes com humanos](https://noticias.uol.com.br/saude/ultimas-noticias/redacao/2020/04/27/respirador-usp-coronavirus.htm)

- _(11/05/2020)_ [Até 50/dia: Marinha inicia produção de ventilador pulmonar barato da USP](https://www.uol.com.br/tilt/noticias/redacao/2020/05/11/ate-50dia-marinha-inicia-producao-de-ventilador-pulmonar-barato-da-usp.htm)

## Outras Mídias

Aqui estão mídias interessantes relacionadas a respiradores e a pandemia em um contexto mais geral.

- _(27/03/2020)_ [Desafios para o suprimento de respiradores para pandemia de covid-19](https://jornal.usp.br/artigos/desafios-para-o-suprimento-de-respiradores-para-pandemia-de-covid-19/)

## Conclusão

Acreditamos que documentar as aparições na mídia seja importante para a transparência do projeto e para o entendimento de como a Universidade e a Escola Politécnica estão se comunicando com a sociedade civil.

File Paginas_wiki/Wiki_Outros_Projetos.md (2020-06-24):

Abaixo estão aglguns outros projetos Open Source que estão desenvolvendo respiradores para o combate à COVID19. Os projetos aqui descritos **não** representam uma recomendação ou opinião oficial da equipe Inspire POLI-USP, mas sim uma lista de projetos que estão sendo desenvolvidos com a mesma finalidade. Devido a problemas jurídicos, o projeto Inspire não pôde ser disponibilizado em sua íntegra.

A seguinte [Lista de projetos ranqueados](https://soptechint.com/ventilators) é uma das melhores fontes para aqueles que gostariam de contribuir para o desenvolvimento de um respirador open source, ou para aqueles que queiram desenvolver um respirador próprio. Vale notar que muitos dos projetos não se aplicam a realidade Brasileira, a exemplo do MIT E-Vent, que como vimos na [análise respirador MIT](https://www.youtube.com/watch?v=m1voC9npYlY&), não poderia ser aprovado na Anvisa por não ser um respirador de malha fechada. Abaixo estão uma Lista de Respiradores Open-Source:

- [Fluxtronic](https://github.com/fluxtronic-medical/Fluxtronic) - Respirador Open Source Brasileiro.

- [EAR-Celso](https://github.com/RespiradorHacker/Projeto-EAR-Celso) - Respirador Open Source Brasileiro, feito com base no MHRA (UK) e no E-Vent (USA), adaptado a realidade brasileira.

- [Ambovent](https://members.smoove.io//view.ashx?message=h44741568O122392748O219654O122323322&r=1009) - Respirador open source Israelense. Esse projeto é conhecido por ser muito aberto e comunicativo com a comunidade Maker.

- [Project Open Air](https://projectopenair.org/pt/open-source-ventilator/) - Respirador Open Source português.

- [Medtronic PB560](http://newsroom.medtronic.com/news-releases/news-release-details/medtronic-shares-ventilation-design-specifications-accelerate) - Ventilador PB560 da empresa médica Medtronic, introduzido em 2010 e vendido e utilizado em mais de 35 países.

- [Corovent](https://www.micomedical.cz/) - Ventilador europeu com design open source, certificado para uso na europa.

- [Mur Project](https://mur-project.org/) - Ventilador open source francês.

- [PAPR](https://github.com/jcl5m1/ventilator) - Ventilador de baixo custo, "Powered Air Purifying Respirator"

- [MakAir](https://github.com/makers-for-life/makair) - Ventilador de baixo custo feito para ser produzido em massa.

Vale notar que a equipe do Inspire Poli USP usou durante o desenvolvimento do projeto as placas Open Source [Caninos Loucos](https://github.com/caninos-loucos), mais especificamente as placas Pulga e Labrador. É possível ver isso nos vídeos relatórios.

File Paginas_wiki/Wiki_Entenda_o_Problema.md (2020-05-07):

# Entenda o Problema

Respiração auxiliada por máquinas é um tópico de estudo da medicina com muitos detalhes. Aqui limitamos enormemente o escopo deste assunto focando em descrever principalmente quais são os os _inputs_ (entradas do sistema) para controle de respiração que um respirador precisa ter.

As informações aqui são a nossa descrição baseada em materiais de estudo, além da síntese de diversas explicações que gentilmente nos foram feitas a respeito deste assunto por profissionais da área (médicos, fisioterapeutas e engenheiros de equipamentos de ventilação mecânica).

Não deixe também de coletar feedback com profissionais da saúde especialistas no tema que você tem alcance. Caso colete alguma informação que acha que estamos ignorando, por favor, abra um [Issue](https://github.com/Inspire-Poli-USP/Inspire-OpenLung/issues) sobre o assunto ou se manifeste no [chat em grupo no Telegram](https://t.me/openlungpoliusp) ou na [nossa lista de emails](https://groups.google.com/forum/#!forum/inspireopenlung).

* * *

## Índice

1.  [A Curva de Respiração](#a-curva-de-respiração)</br>
    1.1. [Intervalos](#intervalos)</br>
    1.1.1. [Como é na prática](#como-e-na-pratica)</br>
    1.2. [Pressões](#pressões)
2.  [O que o Respirador precisa fazer](#o-que-o-respirador-precisa-fazer)
3.  [Como a abordagem mecânica de vocês faz esse controle?](#como-a-abordagem-mecânica-de-vocês-faz-esse-controle)
4.  [E o volume?](#e-o-volume)
5.  [E se o paciente começar a querer respirar no meio disso tudo?](#e-se-o-paciente-começar-a-querer-respirar-no-meio-disso-tudo)
    5.1. [Variáveis de cada paciente](#varáveis-de-cada-paciente)
6.  [Definição do tipo do nosso respirador](#definição-do-tipo-do-nosso-respirador)

* * *

## A Curva de Respiração

A respiração é uma oscilação e pressão e volume do pulmão. Um ventilador precisa reproduzir essa oscilação pelo paciente quando ele tem dificuldade para respirar sozinho, mudando a pressão e volume de ar dentro do pulmão numa frequência específica.

Na medicina existem duas tradições de escolha de variável para se observar durante a respiração auxiliada pelo respirador: a variação de volume inserido no pulmão do paciente ou a variação de pressão no pulmão do paciente. Apesar de haverem supostas vantagens na escolha de uma dessas variáveis, elas são intercambiáveis para fins de monitoramento. No nosso projeto medimos a pressão. Usamos os valores medidos para testar se nossos algoritmos de controle conseguem reproduzir uma curva de respiração com medida de pressão. A tecnologia médica de respiração artificial usa tradicionalmente medidas de milímetros de água (mmH2O) para quantificar a pressão.

### Intervalos

A **curva de respiração** abaixo mostra as diferentes faixas temporais que a compõem:
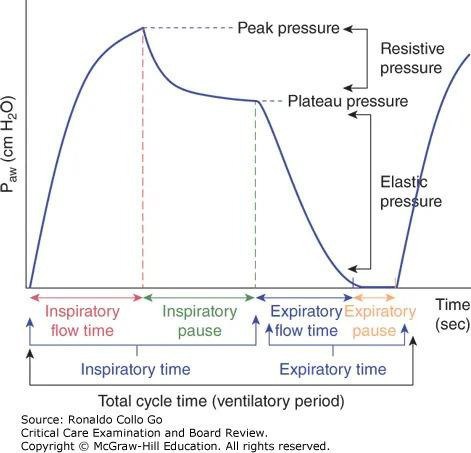
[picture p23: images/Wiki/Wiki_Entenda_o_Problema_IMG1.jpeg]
Curva de respiração baseada em pressão


A imagem acima mostra claramente 4 inputs de intervalos de tempo:

-   Tempo de Inspiração
-   Tempo de Pausa da Inspiração
-   Tempo de Expiração
-   Tempo de Pausa da Expiração

O tempo total desses inputs define a **frequência respiratória** (respirações por minuto). Em muitos casos os tempos individuais de cada uma dessas fases é "padrão", sendo aumentados ou diminuídos de maneira proporcional conforme input do operador do equipamento. Esse input pode ser simples, com o operador apenas definindo o tempo total da respiração através da frequência respiratória, ou mais complicado, com o operador definindo todos os tempos.

#### Como é na prática

Uma maneira muito comum de definir a relação entre esses tempos é uma chamada "proporção" Inspiração/Expiração - em que "Inspiração" é o "Tempo de Inspiração" mais "Tempo de Pausa da Inspiração", e "Expiração" é o "Tempo de Expiração" mais o "Tempo de Pausa da Expiração". Existem por exemplo diferentes recomendações de proporções I/E sugeridas para diferentes tipos de pacientes. Por exemplo: 1:1; 1:2 e etc.

Exemplo prático: se a recomendação para um paciente é 30 ciclos de respiração por minuto, numa relação I/E de 1:2, qual tempo inspiratório e expiratório o fisioterapeuta deve colocar no painel do respirador? Vejamos: 60 segundos/30 ciclos = 2 segundos por ciclo. Como a proporção é 1:2, a inspiração será 0,66 segundos e a expiração será 1,33 segundos.

A interface com o operador é que determinará o nível de especificidade desses inputs. Como essa interface [foge um pouco do nosso escopo](https://github.com/Inspire-Poli-USP/Inspire-OpenLung#onde-queremos-chegar), apenas estamos deixando possível no nosso algoritmo de controle a modificação todos os valores das variáveis de tempo indicadas no gráfico anterior.

Contudo, a título de informação, entendemos pelos feedbacks com especialistas que em ventiladores mais simples o que se define em geral é o tempo total de inspiração (e a proporção entre "Tempo de Inspiração" e "Tempo de Pausa de Inspiração") e a proporção I/E. Com esses dois valores é possível se obter a frequência de respiração (ciclos por minuto) e o tempo total de expiração. Em equipamentos mais completos existe a opção de definir todos os tempos. Caso queira saber quais são esses tempos que geralmente são usados, indicamos [essa referência](https://accessmedicine.mhmedical.com/content.aspx?bookid=520&sectionid=41692246#57062937).

### Pressões

A curva possui 3 inputs de pressão:

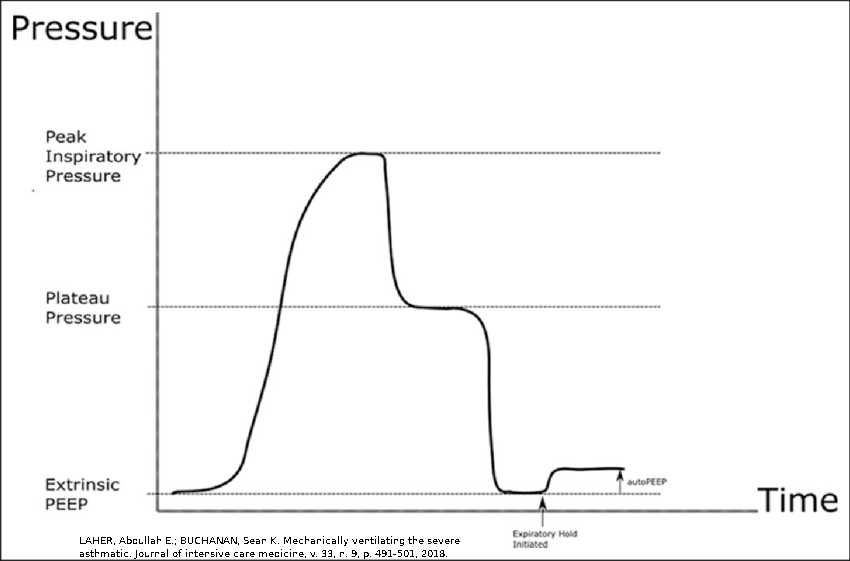
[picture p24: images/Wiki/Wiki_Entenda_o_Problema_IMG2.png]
Pressões da Curva


-   Pressão Máxima de inspiração, a PIP (_Peak Inspiratory Pressure_ - Pressão Inspiratória de Pico)
-   Pressão de Platô, a PP (_Plateau Pressure_)
-   Pressão Expiratória Final Positiva, a "PEEP" (_Positive End-Expiratory Pressure_)

## O que o Respirador precisa fazer

Dados todos os inputs acima, o respirador precisa basicamente reproduzir a curva de respiração que o operador determinar. Além disso, a máquina precisa conseguir gerar valores máximos e mínimos de pressão, conforme definido por [especificações](https://github.com/Inspire-Poli-USP/Inspire-OpenLung#principais-especifica%C3%A7%C3%B5es) de agências governamentais e especialistas da área.

## Como a abordagem mecânica de vocês faz esse controle?

Você talvez já tenha visto que usamos [um motor de passo pressionando um Ambu](https://github.com/Inspire-Poli-USP/Inspire-OpenLung/blob/master/images/Version%205.jpg). Dependendo da velocidade e aceleração com que o Ambu é apertado pelo motor de passo, ele assopra quantidades diferentes de ar em tempos específicos. Isso faz variar a pressão interna no pulmão também de maneira específica, e [conseguimos gerar variações de pressão bem precisas e estáveis, reproduzindo as curvas de respiração](https://www.youtube.com/watch?v=nd0AW7TLXrk), sem usar válvulas que façam o controle ativo dessa pressão. A única válvula usada é a válvula unidirecional passiva, que impede que o ar seja enviado de volta ao Ambu uma vez empurrado para o pulmão.

Outros designs usando outros tipos de motores ou sistemas mecânicos "fixos" não são capazes de fazer um controle preciso para reproduzir a curva de respiração com total flexibilidade.

## E o volume?

Não vamos usar medidores de vazão porque são caros ou imprecisos, quando baratos. Como o ambu não se deforma com o tempo e o motor de passo se move de maneira muito precisa, podemos estimar indiretamente **com precisão** o volume sendo expelido pelo Ambu em função do quanto o motor gira. Validamos isso experimentalmente usando um medidor profissional de vazão de gás.
Assim podemos além de informar gráficos como os anteriores (de pressão ao longo do tempo), mostrar também gráficos de volume ao longo do tempo, contemplando ambas as tradições médicas de monitoramento.

## E se o paciente começar a querer respirar no meio disso tudo?

Durante o processo de retirada gradual do paciente sedado do aparelho de respiração (o "desmame"), o paciente pode fazer tentativas de respirar rozinho.

A PEEP acaba variando dentro de um intervalo durante a respiração sem que o paciente respire ativamente. Se o paciente tentar inspirar, mesmo que levemente, o sensor de pressão detectará uma pequena queda abrupta na PEEP. Se essa queda passar de um limiar fora do intervalo esperado de variação da PEEP, o sistema de controle deve iniciar um novo ciclo de respiração.
Por isso existe **mais um "input" de pressão** do programa de controle, a **pressão limiar de gatilho**, ou **trigger pressure**, que pode ser ativado durante o **Tempo de Pausa da Expiração**. Se houver a ativação do "gatilho" devido a uma queda de pressão ANTES de terminar o Tempo de Pausa da Expiração, um novo ciclo de respiração deve começar imediatamente.

### Variáveis "de cada paciente"

Cada paciente é diferente. O sistema de controle da respiração precisa levar essas diferenças em conta. Na medicina essas diferenças são "medidas" com duas variáveis: **resistência** das vias respiratórias e **complacência** do pulmão. Ou seja: o quão fácil é para uma pessoa inspirar e expirar (resistência das vias respiratórias) e o quanto de ar alguém consegue acumular no pulmão com uma determinada diferença de pressão criada (complacência do pulmão) são coisas que variam de pessoa para pessoa.

No [comentário do @alberiolima no issue #42](https://github.com/Inspire-Poli-USP/Inspire-OpenLung/issues/42#issuecomment-612409353), a "força" que um paciente deve fazer para expirar está relacionada com essas duas variáveis de resistẽncia e complacência.

Um dos [algoritmos de controle](https://github.com/Inspire-Poli-USP/Inspire-OpenLung/issues/26) que usamos, por exemplo, estima através de modelos matemáticos a resistência e a complacência do paciente enquanto a respiração ocorre. Essas estimativas são usadas para **adaptar os ciclos de respiração àquele paciente em particular** - o que também responde à dúvida da comunidade no [Issue #45](https://github.com/Inspire-Poli-USP/Inspire-OpenLung/issues/45#issue-599523947).

## Definição do tipo do nosso respirador

Seguindo as definições formais usadas em medicina, o que descrevemos nesta página é um projeto de respirador...

-   **Gerador de Força Constante** - fluxo variável com as condições de complacência e resistência do sistema respiratório do paciente.
-   de **Ciclagem por Pressão** - um sensor de pressão aciona o controle de insuflação do pulmão conforme a pressão varia.
-   de **Desinsuflação Modulada** - o sistema permite uma desinsuflação passiva até um certo nível, para deixar um pouco de volume nos pulmões, mantendo um determinado nível de PEEP desejado.
-   **Assisto-Controlador de Disparo de Ciclagem E/I** (Expiração/Inspiração) - o sistema pode ou não habilitar um "trigger" de detecção de esforço de respiração do paciente.

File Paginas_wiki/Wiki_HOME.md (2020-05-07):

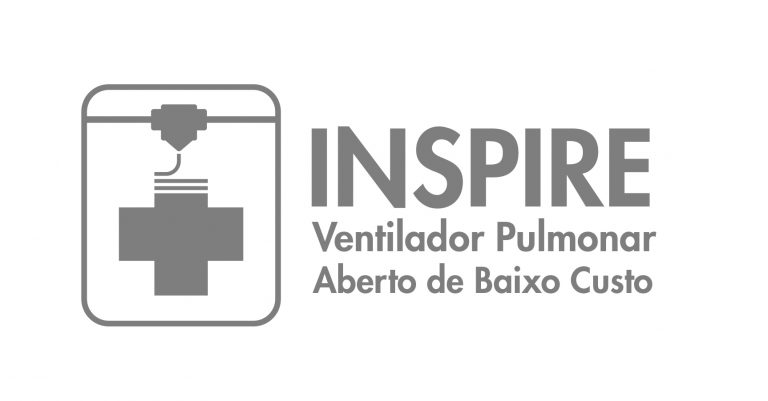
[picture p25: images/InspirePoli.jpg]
Inspire Poli-USP


**Inspire OpenLung é um projeto de respirador Open Source de baixo custo, fabricação rápida e de fácil montagem para uso em casos extremos, durante a ausência de respiradores comerciais.**

Seja bem vindo à wiki do projeto Inspire Poli-USP!

Essa wiki é a principal fonte de informações técnicas voltadas a **desenvolvedores** trabalhando ou contribuindo no projeto. Se essa é a primeira vez que você ouve sobre o Inspire OpenLung da Poli-USP, recomendamos começar pelo [site oficial do projeto](https://www.poli.usp.br/inspire).

Aqui também é o local de registro de relatórios do projeto, organizado por páginas contendo informações sobre o desenvolvimento ao longo dos dias. Estamos correndo contra o tempo, mas vamos tentar deixar esta wiki atualizada o melhor que pudermos.
Você pode selecionar qualquer uma das páginas através do menu à direita.

## Questões ou precisando de ajuda?

Entre em contato por [nosso formulário](https://forms.gle/koJ3gc2z2RKgDynZ6) ou pelo email [inspire@usp.br](mailto:inspire@usp.br)

## Quer contribuir a Wiki?

Saiba mais [aqui](https://github.com/Inspire-Poli-USP/Inspire-OpenLung/tree/master/Paginas_wiki).

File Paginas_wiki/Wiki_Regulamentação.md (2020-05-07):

# Regulamentação

Esta página contém informações sobre a regulamentação necessária para um respirador feito com o projeto deste repositório ser devidamente usado em pacientes com COVID-19 numa situação emergencial.

As informações aqui são a síntese da discussão em aberto no [Issue nº 14](https://github.com/Inspire-Poli-USP/Inspire-OpenLung/issues/14) deste projeto e serão atualizadas conforme evolução dos acontecimentos.

:warning: :warning: :warning: As informações aqui não endorsam quaisquer ações de terceiros usando tais informações ou têm a intenção de substituir qualquer orientação jurídica necessária para a validação de qualquer tentativa de regulamentação de um produto que contenha completa ou parcialmente as informações deste repositório. :warning: :warning: :warning:

:exclamation::exclamation::exclamation: Esta página é responsabilidade de seus autores e não representa a opinião oficial da iniciativa Inspire até que seja explicitamente comunicado o contrário. :exclamation::exclamation::exclamation:

## O que sabemos até agora

A quantidade de normas é grande. Uma possibilidade de realizar todos ou a maioria dos testes necessários a tempo pode ser através da paralelização de diferentes testes por diferentes pessoas, usando reproduções fiéis de um mesmo protótipo.

Outra possibilidade é destrinchar todos os testes necessários e dialogar de maneira propositiva com as agências de regulamentação e autoridades governamentais.

### Lista de Normas

Através da discussão no [Issue 14](https://github.com/Inspire-Poli-USP/Inspire-OpenLung/issues/14), existe a seguinte lista de normas que o ventilador emergencial precisará (links e informações adicionais providos pelo @ArturGasparetto):

1.  [ABNT NBR IEC 60601-1:2010](https://www.abntcatalogo.com.br/norma.aspx?ID=80437) - Equipamento eletromédico - Parte 1: Requisitos gerais para segurança básica e desempenho essencial

2.  [ABNT NBR IEC 60601-1:2010 Emenda 1:2016](https://www.abntcatalogo.com.br/norma.aspx?ID=355495) - Equipamento eletromédico - Parte 1: Requisitos gerais para segurança básica e desempenho essencial

3.  [ABNT NBR IEC 60601-1-2:2017](https://www.abntcatalogo.com.br/norma.aspx?ID=383029) - Equipamento eletromédico - Parte 1-2: Requisitos gerais para segurança básica e desempenho essencial - Norma Colateral: Perturbações eletromagnéticas - Requisitos e ensaios

4.  [ABNT NBR IEC 60601-1-6:2011 Versão Corrigida 2013](https://www.abntcatalogo.com.br/norma.aspx?ID=307130) - Equipamento eletromédico - Parte 1-6: Requisitos gerais para segurança básica e desempenho essencial - Norma colateral: Usabilidade

5.  [ABNT NBR IEC 60601-1-8:2014 Versão Corrigida 2015](https://www.abntcatalogo.com.br/norma.aspx?ID=348135) - Equipamento eletromédico - Parte 1-8: Requisitos gerais para segurança básica e desempenho essencial - Norma colateral: Requisitos gerais, ensaios e diretrizes para sistemas de alarme em equipamentos eletromédicos e sistemas eletromédicos

6.  [ABNT NBR IEC 60601-1-10:2010 Versão Corrigida 2013](https://www.abntcatalogo.com.br/norma.aspx?ID=307136) - Equipamento eletromédico - Parte 1-10: Requisitos gerais para segurança básica e desempenho essencial - Norma colateral: Requisitos para o desenvolvimento de controladores fisiológicos em malha fechada

7.  [ABNT NBR IEC 60601-1-10:2010 Emenda 1:2017](https://www.abntcatalogo.com.br/norma.aspx?ID=371257) - Equipamento eletromédico - Parte 1-10: Requisitos gerais para segurança básica e desempenho essencial — Norma colateral: Requisitos para o desenvolvimento de controladores fisiológicos em malha fechada

8.  [ABNT NBR ISO 80601-2-12:2014](https://www.abntcatalogo.com.br/norma.aspx?ID=326196) - Equipamento eletromédico - Parte 2-12: Requisitos particulares para a segurança básica e o desempenho essencial de ventiladores para cuidados críticos

_Obs.: As normas técnicas listadas acima foram aprovadas pela Instrução Normativa do Ministério da Saúde nº 49 de 27 de Novembro de 2019 (IN 49 Ministério da Saúde-NOVEMBRO DE 2019.pdf), cujos parâmetros devem ser adotados para a certificação de conformidade, no âmbito do Sistema Brasileiro de Avaliação da Conformidade (SBAC), dos equipamentos sob regime de Vigilância Sanitária._

9.  [ABNT NBR ISO 14971:2009](https://www.abntcatalogo.com.br/norma.aspx?ID=55540) - Produtos para a saúde — Aplicação de gerenciamento de risco a produtos para a saúde

10. [ABNT NBR ISO TR 24971:2014](https://www.abntcatalogo.com.br/norma.aspx?ID=325424) - Produtos para a saúde - Orientações para a aplicação da ABNT NBR ISO 14971

11. [ABNT NBR IEC 62366: 2016](https://www.abntcatalogo.com.br/norma.aspx?ID=354941) - Produtos para a saúde — Aplicação da engenharia de usabilidade a produtos para a saúde

### Priorização e Simplificação

A ANVISA está priorizando a análise de [Certificação de Boas Práticas de Fabricação](http://portal.anvisa.gov.br/noticias/-/asset_publisher/FXrpx9qY7FbU/content/esclarecimentos-sobre-priorizacao-de-cbpf-e-produtos/219201).

Tal certificado por inclusive ser substituído por uma certificação do Programa de Auditoria Única para Dispositivos Médicos, e a ausência de alguns requisitos exigidos pelas [normas](#lista-de-normas) podem ser aceitos se devidamente justificados. Ambas informações [segundo o site da ANVISA](http://portal.anvisa.gov.br/noticias/-/asset_publisher/FXrpx9qY7FbU/content/simplificada-a-regularizacao-de-epis-e-outros-produtos/219201?p_p_auth=fY2YVI6E&inheritRedirect=false&redirect=http%3A%2F%2Fportal.anvisa.gov.br%2Fnoticias%3Fp_p_auth%3DfY2YVI6E%26p_p_id%3D101_INSTANCE_FXrpx9qY7FbU%26p_p_lifecycle%3D0%26p_p_state%3Dnormal%26p_p_mode%3Dview%26p_p_col_id%3D_118_INSTANCE_KzfwbqagUNdE__column-2%26p_p_col_count%3D2).

Além do @ArturGasparetto, contribuíram gentilmente com estas informações @buenow e @guiriole.

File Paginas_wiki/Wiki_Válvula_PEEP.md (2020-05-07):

# Ajuda da Comunidade com a Válvula PEEP

Estamos desenvolvendo nossa própria solução, mas também acreditamos que a comunidade pode desenvolver uma solução **mais rapidamente e talvez melhor do que a nossa**.

Dê uma olhada no [Issue #43](https://github.com/Inspire-Poli-USP/Inspire-OpenLung/issues/43) para informações mais atualizadas sobre o desenvolvimento da válvula PEEP. Felizmente recebemos ótimas recomendações da comunidade, muitas das contribuições discutidas no Issue #43 podem ser encontradas no fim dessa página.

## Restrições

Ainda não podemos divulgar nossa solução online devido a [possíveis problemas jurídicos](https://github.com/Inspire-Poli-USP/Inspire-OpenLung#exclamation-atualiza%C3%A7%C3%A3o-importante-exclamation) envolvendo tecnologias potencialmente proprietárias, mas esperamos logo poder compartilhá-las depois do aval de especialistas.

## Prazo

Inicialmente essa ajuda da comunidade foi lançada como um desafio, com prazo até dia 15 de Abril. Esse prazo foi dado para podermos já usar essa nova válvula [em experimentos em animais](https://www1.folha.uol.com.br/colunas/monicabergamo/2020/04/ventilador-da-poli-sera-testado-em-animais-e-pessoas-e-pode-ser-lancado-em-uma-semana.shtml?origin=folha#comentarios).

Desenvolvemos uma solução que ainda pode melhorar, então por isso abrimos o problema para que a comunidade pudesse colaborar.

## Descrição

   A válvula que controla a pressão PEEP ([mais info sobre a PEEP aqui](https://github.com/Inspire-Poli-USP/Inspire-OpenLung/wiki/Entenda-o-Problema#press%C3%B5es)) que estamos usando não aguenta uso prolongado (você pode vê-la [nesse vídeo que fizemos](https://www.youtube.com/watch?v=mwwxAkmB0J0&feature=youtu.be) - é a parte com peças plásticas laranjas). Após cerca de 30min de funcionamento contínuo, começa a ficar imprecisa - ou seja: ela mantém uma PEEP diferente da que indicada pelo marcador. Além disso sua resolução é muito pequena, podendo ser regulada para, por exemplo: 5 cmH2O, 10 cmH20 ou 15 cmH2O, mas não valores entre estes (Como 12 cmH20 ou 7cmH20, por exemplo).

   A regulação da PEEP com mais liberdade pelos fisioterapeutas e médicos é muito importante para determinar a PEEP ideal para cada paciente (chamada de "Titulação de PEEP"). Essa PEEP ideal evita barotraumas e melhora a oxigenação alveolar, o que é crítico para pacientes com COVID-19. Por isso, desenvolver uma solução que melhore a válvula PEEP é crucial para o projeto.

## Problemas a se resolver

-   Imprecisão da válvula PEEP
-   Baixa resolução da válvula PEEP
-   Controle rudimentar (manual)

## Objetivos

  Sem deixar de seguir nossos [princípios e abordagem](https://github.com/Inspire-Poli-USP/Inspire-OpenLung/blob/master/Principios_e_abordagem.md), precisamos que você desenvolva propostas de válvulas PEEP com as seguintes funcionalidades:

-   Ser acionada eletronicamente;
-   Ser capaz de atuar em um intervalo de pressão de pelo menos 5 cmH2O à 15 cmH2O;
-   Ter uma resolução de controle de no mínimo 1 cmH2O - ou seja, podendo ter valores de 5,6,7,8 ..., 13, 14, 15 cmH2O;
-   Ter precisão nos valores configurados - ou seja, por exemplo: selecionar uma pressão de 7 cmH2O deve manter uma medida de pressão **real** de 7 cmH20;
-   Ter uma velocidade de mudança de valores de pressão de no mínimo 1 cmH2O por segundo;
-   Capaz permitir uma vazão de até 600 mL por segundo;
-   Garantir a performance de controle ao longo do tempo - por exemplo: o valor de pressão PEEP selecionado não pode mudar de valor depois de 30min de uso;
-   Usar materiais baratos e acessíveis - por exemplo: peças automotivas;
-   Não violar propriedade intelectual existente - por exemplo: patentes.

## Recursos Necessários

Para este desafio assumimos que você tem acesso a:

-   Alguma maneira de criar uma pressão de ar, como por exemplo:
    -   Bomba de ar,
    -   Assoprador,
    -   Cilindro de ar comprimido, etc;
-   Alguma maneira de medir pressão, por exemplo:
    -   Sensores eletrônicos de pressão,
    -   Coluna de água num tubo transparente, etc;
-   Eletrônica de prototipagem rápida para testes de controle da sua válvula PEEP, por exemplo:
    -   Arduino (qualquer modelo).

## Entregas

Ajudar nesse desafio significa que você vai entregar completa ou parcialmente:

-   Imagens ou vídeos que mostrem como funciona o seu sistema;
-   Especificações dos materiais que vocẽ usou;
-   Gráficos e tabelas com dados que você mediu;
-   Códigos de controle usados nos testes que você fez.

## Local de Discussão

Coloquem suas propostas, dados de medição, fotos, links para vídeos, desenhos, especificações e quaisquer outras informações relacionadas a este desafio no [Issue #43](https://github.com/Inspire-Poli-USP/Inspire-OpenLung/issues/43).

-   Se você não tem uma conta no github, crie e uma e contribua por lá! Essa parte do repositório funciona como um fórum de internet, então não se preocupe por enquanto com "commits", "pull-requests" e outros "palavrões" do github.
-   Você também pode discutir [pelo Telegram](https://t.me/openlungpoliusp), mas não coloque informações lá em detrimento do [Issue #43](https://github.com/Inspire-Poli-USP/Inspire-OpenLung/issues/43). O [Issue #43](https://github.com/Inspire-Poli-USP/Inspire-OpenLung/issues/43) é o melhor lugar para todos acompanharem de uma maneira rápida e mais organizada o que você está fazendo, além de deixar minimamente registrado neste repositório a sua contribuição.

# Como Resultados serão apresentados

Ajudando nesse desafio, a sua válvula pode ser potencialmente usada [nos testes que faremos essa semana](https://www1.folha.uol.com.br/colunas/monicabergamo/2020/04/ventilador-da-poli-sera-testado-em-animais-e-pessoas-e-pode-ser-lancado-em-uma-semana.shtml).

Reconheceremos publicamente sua contribuição caso a usemos como solução principal, além de ficarmos pessoalmente muito gratos por sua boa vontade em ajudar e gentileza em contribuir.

Caso sua contribuição não acabe sendo usada no final, com certeza ela contribuirá para acelerarmos nosso desenvolvimento. É impossível testarmos todas as possibilidades ao mesmo tempo, mas é importante que a maioria delas sejam testadas por vocês

Além disso, a sua contribuição estimula que este projeto seja cada vez mais aberto, [apesar das restrições](https://github.com/Inspire-Poli-USP/Inspire-OpenLung#exclamation-atualiza%C3%A7%C3%A3o-importante-exclamation).

# :warning: Avisos Importantes :warning:

-   Este "desafio" não representa qualquer compromisso da iniciativa Inspire, como por exemplo, mas não limitando-se a, acatar, orientar ou auxiliar quaisquer propostas sobre o exposto nesta página.
-   A iniciativa Inspire não se responsabiliza por quaisquer danos materiais ou prejuízos financeiros que possam ocorrer a qualquer pessoa que use o disposto nesta página para qualquer finalidade. Também não se responsabiliza por quaisquer acidentes que ocorram durante quaisquer ações de pessoas pautadas direta ou indiretamente pelas informações dispostas nesta página.
-   Se você souber de quaisquer ações que estejam sendo tomadas por pessoas usando as informações dispostas nessa página, que direta ou indiretamente possam colocar em risco a segurança e saúde de qualquer ser humano ou animal, recomendamos fortemente que denuncie a autoridades competentes da sua localidade.

# Resultados

  Primeiramente gostariamos de agradecer a todos que dispuseram a contribuir para o projeto nesse repositório, e comentaram no [Issue #43](https://github.com/Inspire-Poli-USP/Inspire-OpenLung/issues/43). Toda contribuição nesse repositório é de extrema ajuda, e nos motiva a manter o repositório movimentado e com as devidas atualizações sobre o projeto! Abaixo estão algumas das contribuições nesse repositório que mais contribuiram para o desenvolvimento da solução atual (Todas elas foram muito boas, principalmente por fomentar a discussão nas Issues).

  Tivemos soluções submetidas pelos seguintes usuários [VitorFrost](https://github.com/Inspire-Poli-USP/Inspire-OpenLung/issues/43#issuecomment-614904015), [adalmirabdala](https://github.com/Inspire-Poli-USP/Inspire-OpenLung/issues/43#issuecomment-612733690), [felipeosi](https://github.com/Inspire-Poli-USP/Inspire-OpenLung/issues/43#issuecomment-614931211), [Imsrv](https://github.com/Inspire-Poli-USP/Inspire-OpenLung/issues/43#issuecomment-614984436)e [GustavoMutra](https://github.com/Inspire-Poli-USP/Inspire-OpenLung/issues/43#issuecomment-615903073).  Todas ajudaram muito no desenvolvimento, por fomentarem um ambiente de discussão e aprendizato na issue. Por fim [foi desenvolvido nesse repositório](https://github.com/Inspire-Poli-USP/Inspire-OpenLung/issues/43#issuecomment-614721287) uma solução seguindo a ideia do VitorForst. Acreditamos que a solução usada atinja os objetivos mencionados, resolvendo os problemas de imprecisão e baixa resolução da válvula PEEP.

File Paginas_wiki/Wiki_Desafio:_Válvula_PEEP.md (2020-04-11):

# Desafio: Válvula PEEP

Quer ajudar tecnicamente? Agora é uma excelente oportunidade!

Estamos desenvolvendo nossa própria solução, mas também acreditamos que a comunidade pode desenvolver uma solução **mais rapidamente e talvez melhor do que a nossa**.

:point_down: Dê uma olhada abaixo para entender a "missão"! :point_down:

## Prazo
:point_right: Até quarta, dia 15 de Abril :point_left:

## Descrição
   A válvula que controla a pressão PEEP ([mais info sobre a PEEP aqui](https://github.com/Inspire-Poli-USP/Inspire-OpenLung/wiki/Entenda-o-Problema#press%C3%B5es)) que estamos usando não aguenta uso prolongado (você pode vê-la [nesse vídeo que fizemos](https://www.youtube.com/watch?v=mwwxAkmB0J0&feature=youtu.be) - é a parte com peças plásticas laranjas). Após cerca de 30 min de funcionamento contínuo, começa a ficar imprecisa - ou seja: ela mantém uma PEEP diferente da que indicada pelo marcador. Além disso sua resolução é muito pequena, podendo ser regulada para, por exemplo: 5 cmH2O, 10 cmH20 ou 15 cmH2O, mas não valores entre estes. 
   
   A regulação da PEEP com mais liberdade pelos fisioterapeutas e médicos é muito importante para determinar a PEEP ideal para cada paciente (chamada de "Titulação de PEEP"). Essa PEEP ideal evita barotraumas e melhora a oxigenação alveolar, o que é crítico para pacientes com COVID-19.
   
## Problemas a se resolver

  - Imprecisão da válvula PEEP
  - Baixa resolução da válcula PEEP
  - Controle rudimentar (manual)

## Objetivos
  
  Sem deixar de seguir nossa [abordagem e princípios](https://github.com/Inspire-Poli-USP/Inspire-OpenLung/blob/master/Principios_e_abordagem.md), precisamos que você desenvolva propostas de válvulas PEEP com as seguintes funcionalidades:
  
  - Ser acionada eletronicamente;
  - Ser capaz de atuar em um intervalo de pressão de pelo menos 5 cmH2O à 15 cmH2O;
  - Ter uma resolução de controle de no mínimo 1 cmH2O - ou seja, podendo ter valores de 5,6,7,8 ..., 13, 14, 15 cmH2O;
  - Ter precisão nos valores configurados - ou seja, por exemplo: selecionar uma pressão de 7 cmH2O deve manter uma medida de pressão **real** de 7 cmH20;
  - Ter uma velocidade de mudança de valores de pressão de no mínimo 1 cmH2O por segundo;
  - Garantir a performance de controle ao longo do tempo - ou seja: a exemplo da a válvula que estamos usando, o valor de pressão PEEP selecionado não pode mudar de valor depois de 30 min de uso;
  - Usar materiais baratos e acessíveis - por exemplo: peças automotivas;
  - Não violar propriedade intelectual existente.
  
## Recursos Necessários

  Para este desafio assumimos que você tem acesso a:
  - Alguma maneira de criar uma pressão de ar, como por exemplo:
    - Bomba de ar,
    - Assoprador,
    - Cilindro de ar comprimido, etc;
  - Alguma maneira de medir pressão, por exemplo:
    - Sensores eletrônicos de pressão,
    - Coluna de água num tubo transparente, etc;
  - Eletrônica de prototipagem rápida para testes de controle da sua válvula PEEP, por exemplo:
    - Arduino (qualquer modelo).
  
## Entregas

  Ajudar nesse desafio significa que você vai entregar completa ou parcialmente:
  - Imagens ou vídeos que mostrem como funciona o seu sistema;
  - Especificações dos materiais que vocẽ usou;
  - Gráficos e tabelas com dados que você mediu;
  - Códigos de controle usados nos testes que você fez.

## Local de Discussão

  Coloquem suas propostas, dados de medição, fotos, links para vídeos, desenhos, especificações e quaisquer outras informações relacionadas a este desafio no [Issue #43](https://github.com/Inspire-Poli-USP/Inspire-OpenLung/issues/43).
  - Se você não tem uma conta no github, crie e uma e contribua por lá! Essa parte do repositório funciona como um fórum de internet, então não se preocupe por enquanto com "commits", "pull-requests" e outros "palavrões" do github.
  - Você também pode discutir [pelo Telegram](https://t.me/openlungpoliusp), mas não coloque informações lá em detrimento do [Issue #43](https://github.com/Inspire-Poli-USP/Inspire-OpenLung/issues/43). O [Issue #43](https://github.com/Inspire-Poli-USP/Inspire-OpenLung/issues/43) é o melhor lugar para todos acompanharem de uma maneira rápida e mais organizada o que você está fazendo, além de deixar minimamente registrado neste repositório a sua contribuição.
  
# Resultados

Ajudando nesse desafio, a sua válvula pode ser potencialmente usada [nos testes que faremos essa semana](https://www1.folha.uol.com.br/colunas/monicabergamo/2020/04/ventilador-da-poli-sera-testado-em-animais-e-pessoas-e-pode-ser-lancado-em-uma-semana.shtml).

Reconheceremos publicamente sua contribuição caso a usemos como solução principal, além de ficarmos pessoalmente muito gratos por sua boa vontade em ajudar e gentileza em contribuir.

Caso sua contribuição não acabe sendo usada no final, com certeza ela contribuirá para acelerarmos nosso desenvolvimento. É impossível testarmos todas as possibilidades ao mesmo tempo, mas é importante que a maioria delas sejam testadas por vocês

Além disso, a sua contribuição estimula que este projeto seja cada vez mais aberto, [apesar das restrições](https://github.com/Inspire-Poli-USP/Inspire-OpenLung#exclamation-atualiza%C3%A7%C3%A3o-importante-exclamation).

# :warning: Avisos Importantes :warning:

  - Este "desafio" não representa qualquer compromisso da iniciativa Inspire, como por exemplo, mas não limitando-se a, acatar, orientar ou auxiliar quaisquer propostas sobre o exposto nesta página.
  - A iniciativa Inspire não se responsabiliza por quaisquer danos materiais ou prejuízos financeiros que possam ocorrer a qualquer pessoa que use o disposto nesta página para qualquer finalidade. Também não se responsabiliza por quaisquer acidentes que ocorram durante quaisquer ações de pessoas pautadas direta ou indiretamente pelas informações dispostas nesta página.
  - Se você souber de quaisquer ações que estejam sendo tomadas por pessoas usando as informações dispostas nessa página, que direta ou indiretamente possam colocar em risco a segurança e saúde de qualquer ser humano ou animal, recomendamos fortemente que denuncie a autoridades competentes da sua localidade.

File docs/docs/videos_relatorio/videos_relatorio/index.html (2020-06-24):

- Home
- Documentação

 (https://inspire-poli-usp.github.io/Inspire-OpenLung/)

 (https://inspire-poli-usp.github.io/Inspire-OpenLung/)

- Home
- Documentação

#### Docs

- FAQ (https://inspire-poli-usp.github.io/Inspire-OpenLung/docs/faq/faq/)
- Videos Relatorio (https://inspire-poli-usp.github.io/Inspire-OpenLung/docs/videos_relatorio/videos_relatorio/)
- Entenda o problema (https://inspire-poli-usp.github.io/Inspire-OpenLung/docs/entenda_o_problema/entenda_o_problema/)
- Regulamentação (https://inspire-poli-usp.github.io/Inspire-OpenLung/docs/regulamenta%C3%A7%C3%A3o/regulamenta%C3%A7%C3%A3o/)
- Sistema de Testes (https://inspire-poli-usp.github.io/Inspire-OpenLung/docs/sistema_de_testes/sistema_de_testes/)
- Válvula PEEP (https://inspire-poli-usp.github.io/Inspire-OpenLung/docs/v%C3%A1lvula_peep/v%C3%A1lvula_peep/)
- Midia (https://inspire-poli-usp.github.io/Inspire-OpenLung/docs/midia/midia/)
- Outros Projetos (https://inspire-poli-usp.github.io/Inspire-OpenLung/docs/outros_projetos/outros_projetos/)

# Videos Relatorio

Abaixo estão todos os vídeos relatório gravados, em ordem cronológica. Todos os vídeos podem ser encontrados no Canal do YouTube da POLI-USP (https://www.youtube.com/channel/UCJU4uI6j2lfSKkzktwFWQRw). Os interlocutores dos vídeos normalmente são o professor Marcelo Zuffo e o professor Raúl Lima.

# 1 de Abril

Apresentação inicial do INSPIRE, o ventilador pulmonar aberto da USP.

# 2 de Abril

Comentários sobre o trabalho desenvolvido no dia 2 de Abril. Foi apresentado o trabalho desenvolvido pelo Felipe, que foram estimativas da complacência e da resistência do pulmão.

# 6 de Abril

Comentários sobre o algorítmo de controle utilizado no INSPIRE.

# 8 de Abril - Avaliação do projeto de ventilador pulmonar do MIT

Avaliação de uma réplica modificada do ventilador pulmonar do MIT. Foram mostradas sugestões de mudanças para o projeto.

# 8 de Abril

Mostrando avanços, os inspires começaram a ser produzidos. Houve também avanços no algoritmo de controle.

# 9 de Abril

Explicação sobre os softwares utilizados no projeto INSPIRE. Foi utilizado o algoritmo PID, bem como outros algoritmos de controle.

# 11 de Abril

Foram conseguidas melhoras no algoritmo PID. Foi mostrada a última versão do INSPIRE além de comentários sobre a interface gráfica.

# 16 de Abril

Foram mostrados testes de integração e a placa da caninos (labrador).

# 18 de Abril

Foram mostradas uma tela sensível ao toque juntamente com as placas labrador, pulga e speedbase.

# 19 de Abril

Foi mostrado uma versão do inspire com um drive de 24V (DM-542).

# 24 de Abril

Foi o inspire no Instituto do Coração, onde foram feitos os testes com pacientes.

# 25 de Abril

Foi mostrado a ultima versão do inspire juntamente com membros do IFSP.

# 26 de Abril a 1 de Maio

Foi mostrado o início de uma conversa entre o professor Raúl e a Globo, além dos últimos desenvolvimentos do projeto INSPIRE. Foi também mostrado o capacete de respiração do projeto inspire em testes.

# 7 de Maio

Apresentação da última versão disponível do projeto INSPIRE, além de uma demonstração de seu funcionamento em um pulmão artificial.

# 7 de Maio - agradecimento a Mapfre

Vídeo em agradecimento a fundação Mapfre.

# 11 de Maio

Mostrando a montagem de placas

# 16 de Maio

Mostrando a montagem dos respiradores

# 17 de Maio

Teste conceitual para alimentar o inspire com baterias externas

# 20 de Maio

Apresentação do ventilador pulmar inspire, versão 1.0, revisão A. É demonstrado os respectivos alarmes sendo disparados, como requerido pela Anvisa.

# 23 de Maio

Apresentação do time do Inspire, demonstrando o funcionamento do respirador. É também notado que a maioria das peças usadas no Inspire podem ser obtidas no mercado nacional.

- Made with Hugo (https://gohugo.io/), hosted with github pages (https://pages.github.com/)

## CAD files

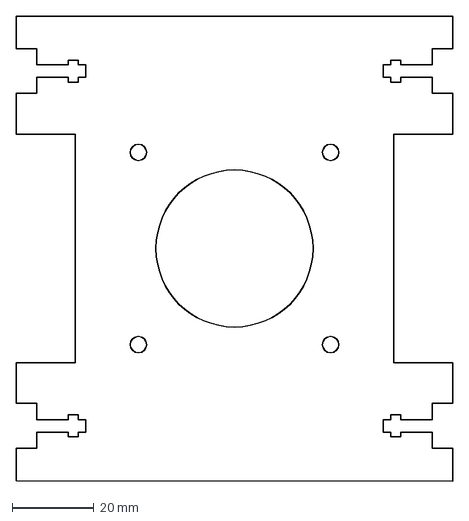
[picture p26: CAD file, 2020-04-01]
2D laser cut/v5/plate motor V5.dxf
107.0 x 114.0 mm

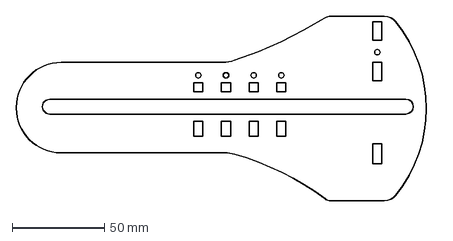
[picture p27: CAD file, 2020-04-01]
2D laser cut/v5/piston V5.dxf
227.7 x 100.0 mm

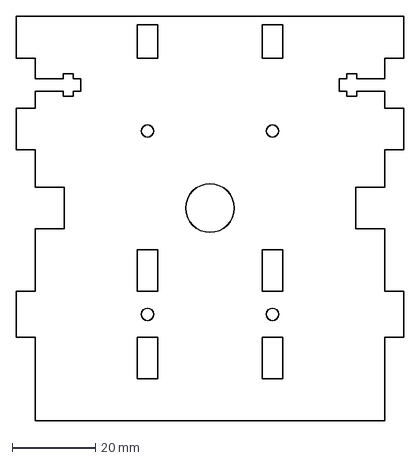
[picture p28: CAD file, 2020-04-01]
2D laser cut/v5/plate piston V5.dxf
93.0 x 97.0 mm

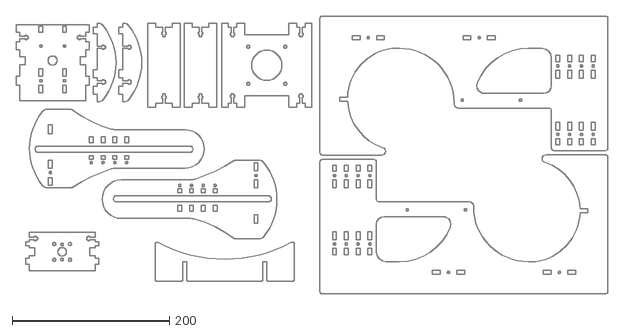
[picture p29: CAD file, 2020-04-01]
2D laser cut/v5/cut V5.dxf
752.4 x 353.4

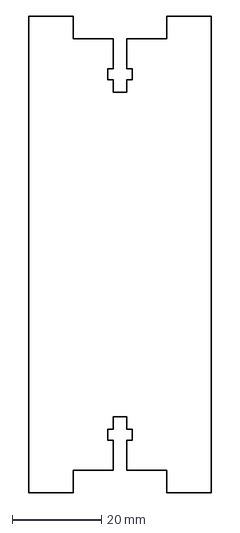
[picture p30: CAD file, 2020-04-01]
2D laser cut/v5/bottom plate V5.dxf
41.0 x 107.0 mm

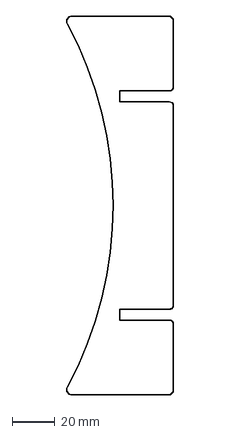
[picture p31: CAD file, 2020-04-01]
2D laser cut/v5/ambu support V5.dxf
50.0 x 177.0 mm

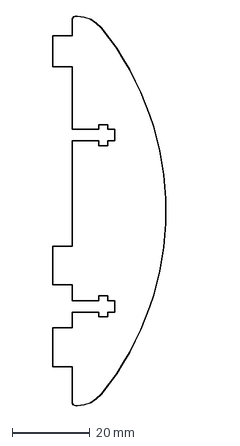
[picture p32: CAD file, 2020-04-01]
2D laser cut/v5/piston support V5.dxf
34.6 x 100.0 mm

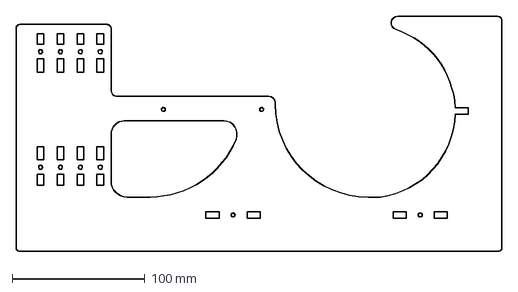
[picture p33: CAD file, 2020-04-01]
2D laser cut/v5/side V5.dxf
366.1 x 177.0 mm

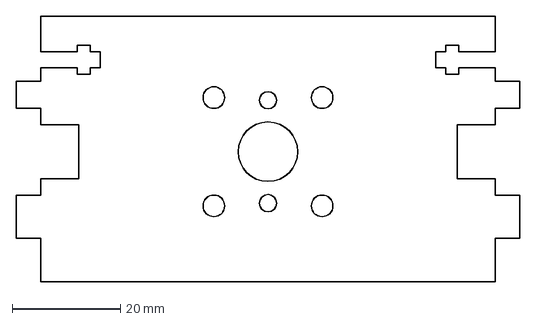
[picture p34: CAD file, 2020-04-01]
2D laser cut/v5/plate nut V5.dxf
93.0 x 49.0 mm

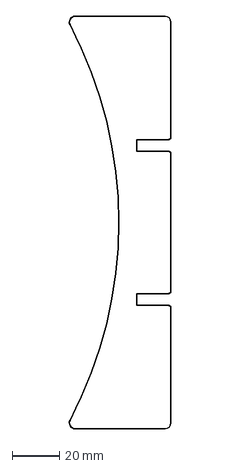
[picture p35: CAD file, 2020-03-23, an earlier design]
2D laser cut/v2.2/ambu support V2.2.dxf
43.0 x 174.0 mm

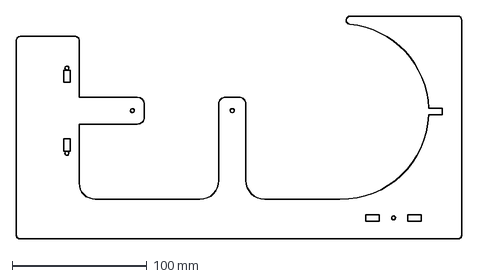
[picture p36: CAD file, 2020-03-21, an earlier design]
2D laser cut/v2/side v2.dxf
330.0 x 165.0 mm

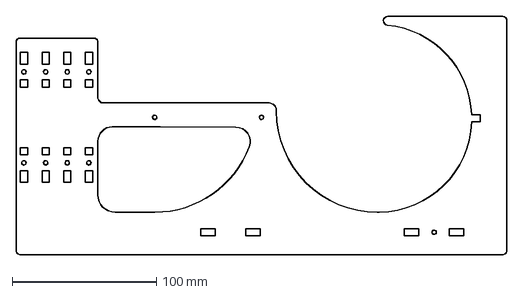
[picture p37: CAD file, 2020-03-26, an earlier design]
2D laser cut/v3/side V3.dxf
340.0 x 165.0 mm

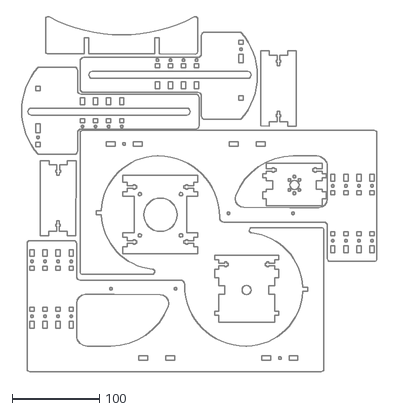
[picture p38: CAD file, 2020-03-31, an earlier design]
2D laser cut/v4.1/all pieces V4.1.dxf
413.3 x 407.2

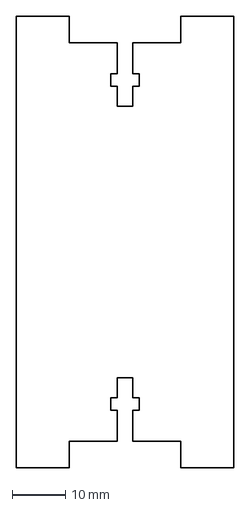
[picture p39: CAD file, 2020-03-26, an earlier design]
2D laser cut/v4/bottom plate V4.dxf
41.0 x 85.0 mm

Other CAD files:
2D laser cut/v2.1/corte.dxf
2D laser cut/v2.1/motor plate V2.1.dxf
2D laser cut/v4/side V4.dxf
2D laser cut/v2.1/ambu support V2.1.dxf
2D laser cut/v2.1/base plate V2.1.dxf
2D laser cut/v2.1/nut plate V2.1.dxf
2D laser cut/v2.1/piston V2.1.dxf
2D laser cut/v2.1/piston plate V2.1.dxf
2D laser cut/v2.1/side V2.1.dxf
2D laser cut/v2.2/base support V2.2.dxf
2D laser cut/v2.2/motor plate V2.2.dxf
2D laser cut/v2.2/nut plate V2.2.dxf
2D laser cut/v2.2/piston V2.2.dxf
2D laser cut/v2.2/piston plate V2.2.dxf
2D laser cut/v2.2/side V2.2.dxf
2D laser cut/v2/base support plate v2.dxf
2D laser cut/v2/nut plate v2.dxf
2D laser cut/v2/piston plate v2.dxf
2D laser cut/v2/plate motor v2.dxf
2D laser cut/v3/bag support V3.dxf
2D laser cut/v3/base plate V3.dxf
2D laser cut/v3/motor plate V3.dxf
2D laser cut/v3/nut plate V3.dxf
2D laser cut/v3/piston V3.dxf
2D laser cut/v3/piston plate V3.dxf
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

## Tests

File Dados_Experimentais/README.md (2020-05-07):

### :exclamation: ATUALIZAÇÃO IMPORTANTE :exclamation:

-   IMPORTANTE: leia sobre [essa atualização crítica](https://github.com/Inspire-Poli-USP/Inspire-OpenLung#exclamation-atualiza%C3%A7%C3%A3o-importante-exclamation), junto com ela retiramos os dados experimentais do projeto por enquanto.

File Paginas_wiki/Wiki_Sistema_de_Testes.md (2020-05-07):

# Sistema de Testes

Para testar o funcionamento do nosso sistema com base [no que nos propomos fazer](https://github.com/Inspire-Poli-USP/Inspire-OpenLung/wiki/Entenda-o-Problema), temos acesso a um sistema padronizado de testes de equipamentos médicos que envolvem ventilação artificial, com o acesso gentilmente cedido pelo prof. Herique Moriya, no Laboratório de Engenharia Biomédica da Poli-USP.

## Nosso sistema

Nosso sistema é o seguinte:

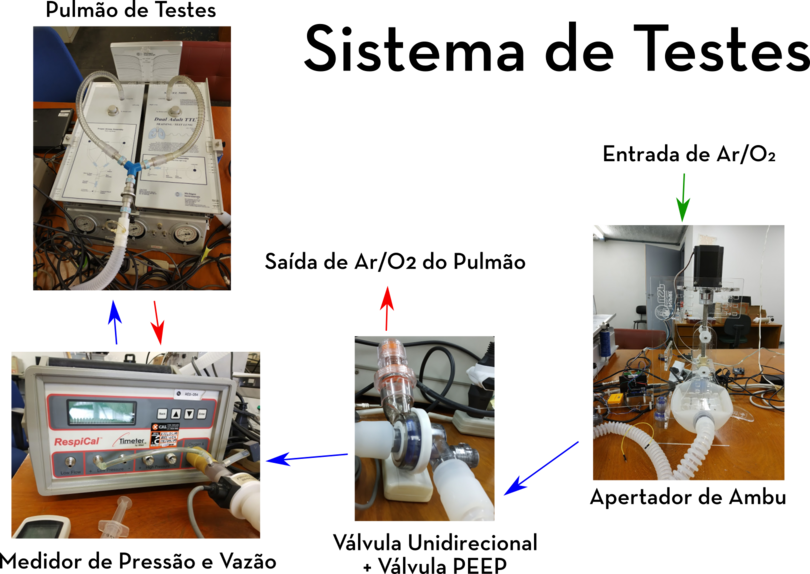
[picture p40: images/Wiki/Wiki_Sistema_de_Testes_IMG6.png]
Esquema do sistema de testes


Cujas especificações são:

-   Pulmão de testes - [Dual Adult PNEU/VIEW System, Model 5600i - Michigan Instruments](https://web.archive.org/web/20200406002510/https://www.michiganinstruments.com/wp-content/uploads/2018/11/5600_manual2.pdf)
    -   Com esse instrumento é possível ajustar finamente a [resistência à passagem de ar das vias aéreas](https://en.wikipedia.org/wiki/Airway_resistance) e a [complacência do pulmão](https://pt.wikipedia.org/wiki/Complac%C3%AAncia_pulmonar).
-   Medidor de Fluxo e Pressão - [Respical Timeter, Model T300 - Allied Healthcare Products](https://web.archive.org/web/20180827132142/http://www.alliedhpi.com/images/z10-00-1000.pdf)
    -   É um equipamento portátil de calibração de respiradores comerciais.
-   Válvula Unidirecional acoplada à Válcula PEEP - [Exemplo](https://web.archive.org/save/https://www.cpaps.com.br/valvula-peep-ajustavel-standard-circuito-cpap)
    -   Vale a pena olhar [este relatório](https://github.com/Inspire-Poli-USP/Inspire-OpenLung/wiki/Relat%C3%B3rio-9%C2%BA-Dia) antes de usá-la.

Alternativamente, é possível usar um pulmão de testes portátil, como o da seguinte foto:

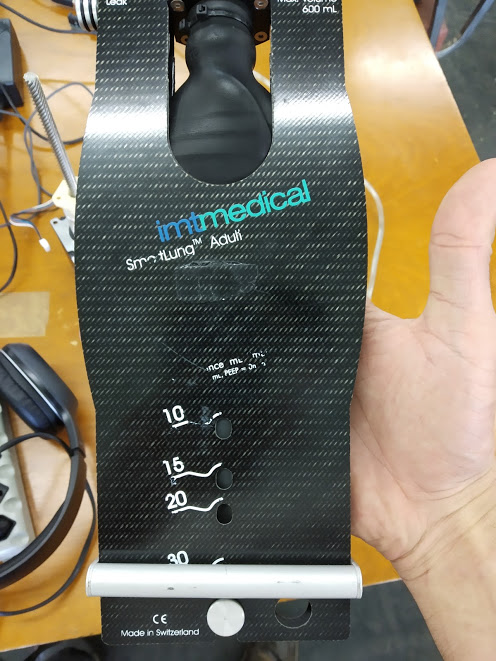
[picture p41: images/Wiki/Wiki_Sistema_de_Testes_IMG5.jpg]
Pulmão de testes portátil


Especificação:

-   Pulmão de teste portátil - [SmartLung, Adult 600 mL - imtmedical](https://web.archive.org/web/20161111052542/https://biomedequip.com/index.php?route=product/product&product_id=156)

Contudo este pulmão de testes é muito mais limitado que o anterior, não sendo o mais tradicionalmente usado para testes de ventiladores.

Em nosso caso, medimos em redundância a pressão do sistema usando outro equipamento. Fazemos isso para garantir a exatidão das medidas e também por problemas envolvendo a extração de dados pelo software desses equipamentos - dica: antecipe/se prepare para encontrar problemas do tipo.

## Sugestão

  Caso você queira replicar nossos testes ou fazer quaisquer outros por conta própria, sugerimos que procure um local com equipamentos semelhantes a estes, que podem ser encontrados em centros de pesquisa e hospitais. Assim seus dados e validações estarão dentro dos padrões de qualidade mais comuns de teste, podendo ser portanto melhor compartilhados.

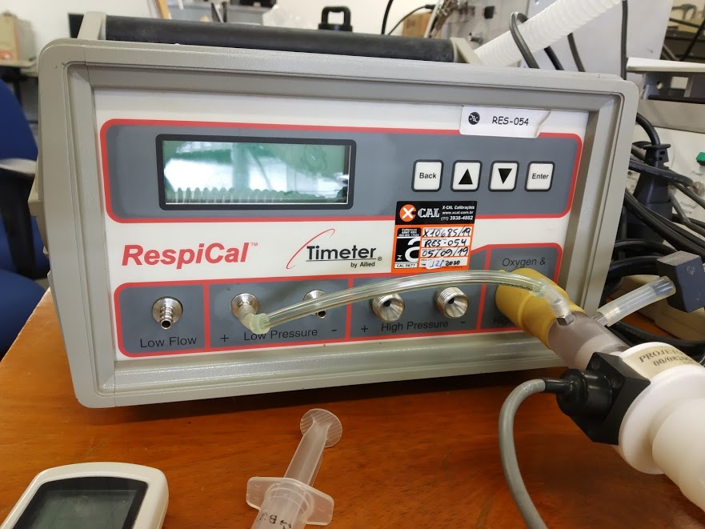
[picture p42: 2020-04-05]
images/Wiki/Wiki_Sistema_de_Testes_IMG2.jpg

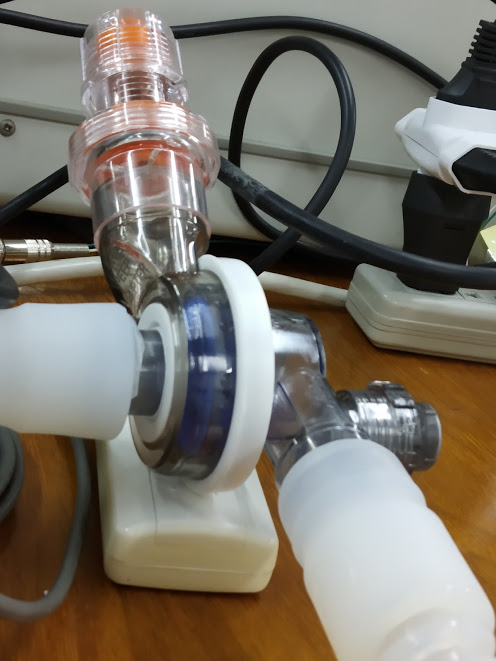
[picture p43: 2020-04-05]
images/Wiki/Wiki_Sistema_de_Testes_IMG3.jpg

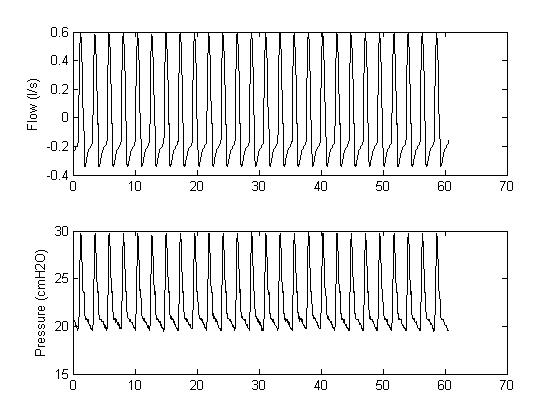
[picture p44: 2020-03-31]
images/Test_2_20_03_2020.jpg

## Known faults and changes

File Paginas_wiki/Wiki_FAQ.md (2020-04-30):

## FAQ

Esse é um FAQ (Frequent asked questions) onde temos uma coletânea das perguntas mais feitas, principalmente em nosso grupo do telegram.

# Quero contribuir, por onde começo?

Primeiramente muito obrigado por querer contribuir! Para contribuir, recomendamos primeiro olhar as [issues](https://github.com/Inspire-Poli-USP/Inspire-OpenLung/issues) atuais e ver se tem algum problema com o qual você se identifique (ou alguma discussão da qual você ache que possa contribuir). Também recomendamos que você entre em nosso [chat em grupo no Telegram](https://t.me/openlungpoliusp). Caso você queira saber mais detalhes, recomendamos a leitura do nosso [guia de como colaborar](https://github.com/Inspire-Poli-USP/Inspire-OpenLung/blob/master/CONTRIBUTING.md).

Você também pode abrir novas issues caso encontre algum problema não solucionado ou tenha alguma sugestão nova em relação ao projeto.

# Posso construir respirador com as informações no repositório?

Não é possível construir um respirador completo com todas as informações presentes nesse repositório.

Nesse braço open source da inciativa inspire pretendemos desenvolver os módulos centrais do ventilador, como o apertador de ambu e o algoritmo de controle. Nesse repositório open source você encontrará somente informações relacionadas ao apertador de ambu e outras informações (como documentação do projeto, discussões diversas sobre válvulas e sensores e esquematização do projeto). O software relacionado ao algoritmo de controle não se encontra nesse projeto por questões jurídicas, interessados em ter acesso e que possam assumir responsabilidades civis devem entrar em contato direto através do email [inspire@usp.br](mailto:inspire@usp.br).

Lembrando, esse é um projeto em desenvolvimento e não deve ser usado em humanos em seu estado atual.

# Como está o projeto em termos regulatórios?

Questões regulatórias são uma dificuldade para todos os projetos de respiradores a serem desenvolvidos para o enfretamento da COVID-19. Para mais informações é recomendável ler a [página na wiki](https://github.com/Inspire-Poli-USP/Inspire-OpenLung/wiki/Regulamenta%C3%A7%C3%A3o) e seguinte [issue](https://github.com/Inspire-Poli-USP/Inspire-OpenLung/issues/14) onde isso foi discutido.

# Tenho alguma dúvida ou sugestão, onde posso entrar em contato?

Pedimos que entre em contato através do nosso [chat em grupo no Telegram](https://t.me/openlungpoliusp) do nosso email [inspire@usp.br](mailto:inspire@usp.br) ou através [desse formulário rápido](https://forms.gle/2u1fxgFx3JDqjxeX7). Nessa fase do projeto a ajuda de empresas ou especialistas é crucial para a finalização do respirador.

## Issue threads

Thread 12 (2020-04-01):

Inspire-Poli-USP/Inspire-OpenLung #12: Oxímetro

atodobom, 2020-04-01:
Seguindo opiniões profissionais, já houve perda de paciente por falta de oxímetro.
O produto aqui tem como objetivo final oxigenar o paciente. Monitores multiparâmetros serão raros na atual demanda.
Estive estudando alguns dispositivos. Mas se a gente tentar usar esses simples apresentam alguns problemas, como utilizar pilhas que não duram mais que 12 horas, e nem sempre se mantém ligados. Quando conectam via bluetooth nem sempre temos o protocolo aberto e problemas de certificação.
Fui atrás de sondas certificadas, encontrei algumas, mas são discretas e basicamente tratam-se de sensores óticos, led, e fototansistor e precisam ter os dados tratados com circuitos conformadores de sinal, e algorítimos complexos para se obter a saturação e pulsação.
Encontrei uma placa muito pequena interessante. Ela é composta dos sensores e já um ARM cortex M0 e saída I2C já com os dados tratados. O problema dela seria construir o suporte mecânico para acoplar ao dedo do paciente, tendo algumas versões conforme idade. E saber o que isso impacta na certificação final do produto. No site apresentam programa de teste para Arduino. É simples, ele envia algumas vezes por segundo os dados de saturação, pulso e um valor que apresenta a qualidade da medição, para caso esteja saindo do dedo gerar um alerta.

VitorFrost, 2020-04-02:
Muito interessante, mas isso não impediria o uso de desfibriladores?

akapmarak, 2020-04-02:
É uma demanda pertinente.
Porém o valor produto final não seria desproporcional?

Um oxímetro está uns 70 reais, já com display. E daria pra adaptar uma fonte de energia.

Diferencial seria uma telemetria com módulos de maior alcance, pra controlar toda uma enfermaria.

atodobom, 2020-04-02:
Problema é um oxímetro desse de R$ 70 com pilha que não dura muito. Sem conexão ele não gera alerta, ao menos não seja chamativo para o ambiente que existirá, e se conectar por bluetooth não sei se acharemos com protocolo aberto, além das possíveis dificuldades quanto a aquisição de determinados modelos etc.
Podemos pensar quando ao material que coloquei, o módulo microcontrolado que possui já o tratamento do sinal e entrega as medidas prontas, ou usar probes hospitalares certificadas e tratar o sinal.
No mercado local, e fabricado aqui tempos as probes que são "compatíveis" com equipamentos.
Trata-se de uma probe para colocar no dedo, contendo led Red e iRed, e fotosensor.

Encontrei o material para tratar o sinal em https://www.bbc.com/portuguese/internacional-40734577

Pessoalmente eu gosto de usar um módulo com ARM que tem várias entradas ADC, seriais, e já tem BLE com antena e tudo. O módulo tem menos de 1 cm², com bom poder computacional.
Seria uma opção, mas me questiono o Time to Market disso.

VitorFrost, 2020-04-02:
Antonio, acredito que o link esteja incorreto.
Verifique se era esta referência: https://www.nxp.com/docs/en/application-note/AN4327.pdf

atodobom, 2020-04-02:
Hauhaua... 
Não acredito que esteja incorreto... eu tenho CERTEZA! 
Sim.. essa AN mesmo. Muita coisa aberta no browser dá nisso! KKKK
Obrigado! Já até editei o comment. Mas assim.
Entendam que são ideias soltas estilo brainstorm, que podem eventualmente ter algum resultado

FlavioAlegretti, 2020-04-05:
Olá pessoal, em alguma parte do projeto pensam em utilizar conversores para acionamento do motor ou estão acionando direto das pilhas? Digo isso pois lendo a discussão percebi a preocupação com as pilhas e talvez um conversor (seria ligado na tomada 127/220 e convertido para 12V, 9V ou 5V) forneceria com pouca utilização de espaço a energia necessária (um conversor flyback estilo utilizado em carregadores de celular), único inconveniente seria ter que ligar na tomada.

closed 2020-04-26 by breno-helf

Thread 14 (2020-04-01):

Inspire-Poli-USP/Inspire-OpenLung #14: ANVISA

m-rodrigues-souza, 2020-04-01:
O que já temos de informação sobre a certificação do produto? Em qual classe ele se enquadra, quais as normas aplicáveis e qual o processo para certificar?

emersonmoretto, 2020-04-01:
Opa, ainda nao temos, estamos validando a capacidade dele de fluxo,
pressao no pulmao artificial da usp e devemos partir pra validacao em
animais e regulaçao a partir de segunda

valeu

*Emerson Moretto*
emerson@moretto.eng.br
11 99484-0571

atodobom, 2020-04-01:
Ao menos as NBR ISO 62366 e 60601-1-6 parecem que precisam ser seguidas.
Aí tem todas aquelas RDC que indicam outras normas.

OttoHeringer, 2020-04-03:
Acabei de receber uma info e docs sobre regulamentação. Vou criar um documento explicativo e fazer upload das normas que temos aqui.
Obrigado por ter criado esse Issue, @atodobom !

OttoHeringer, 2020-04-06:
Um ótimo resumo do tamanho do trabalho que seria fazer isso "normalmente" é esse:

[image]

OttoHeringer, 2020-04-06:
Outra informação que recebi em grupos de whatsapp com pessoas envolvidas com esse trabalho regulatório tem a seguinte listagem de normas (que é basicamente um dos quadradinhos do fluxograma acima):

1. ABNT NBR IEC 60601-1:2010 - Equipamento eletromédico - Parte 1: Requisitos gerais para segurança básica e desempenho essencial

2. ABNT NBR IEC 60601-1:2010  Emenda 1:2016 - Equipamento eletromédico - Parte 1: Requisitos gerais para segurança básica e desempenho essencial
 
3. ABNT NBR IEC 60601-1-2:2017 - Equipamento eletromédico - Parte 1-2: Requisitos gerais para segurança básica e desempenho essencial - Norma Colateral: Perturbações eletromagnéticas - Requisitos e ensaios

4. ABNT NBR IEC 60601-1-6:2011 Versão Corrigida 2013 - Equipamento eletromédico - Parte 1-6: Requisitos gerais para segurança básica e desempenho essencial - Norma colateral: Usabilidade
 
5. ABNT NBR IEC 60601-1-8:2014 Versão Corrigida 2015 - Equipamento eletromédico - Parte 1-8: Requisitos gerais para segurança básica e desempenho essencial - Norma colateral: Requisitos gerais, ensaios e diretrizes para sistemas de alarme em equipamentos eletromédicos e sistemas eletromédicos

6. ABNT NBR IEC 60601-1-10:2010  Versão Corrigida 2013 - Equipamento eletromédico - Parte 1-10: Requisitos gerais para segurança básica e desempenho essencial - Norma colateral: Requisitos para o desenvolvimento de controladores fisiológicos em malha fechada
 
7. ABNT NBR IEC 60601-1-10:2010 Emenda 1:2017 - Equipamento eletromédico - Parte 1-10:
Requisitos gerais para segurança básica e desempenho essencial — Norma colateral: Requisitos para o desenvolvimento de controladores fisiológicos em malha fechada

8 - ABNT NBR ISO 80601-2-12:2014 - Equipamento eletromédico - Parte 2-12: Requisitos particulares para a segurança básica e o desempenho essencial de ventiladores para cuidados críticos

9 - ABNT NBR ISO 14971:2009 - Produtos para a saúde — Aplicação de gerenciamento 
de risco a produtos para a saúde

10 - ABNT NBR ISO TR 24971:2014 - Produtos para a saúde - Orientações para a aplicação da ABNT NBR ISO 14971

11 - ABNT NBR IEC 62366: 2016 - Produtos para a saúde — Aplicação da engenharia de usabilidade a produtos para a saúde

OttoHeringer, 2020-04-06:
Há pessoas comentando sobre a criação de alguma portaria "flexibilizante", como aconteceu nos (lamentáveis) casos da cloroquina e fosfoetanolamina, o que pode ser tanto uma coisa boa como ruim no nosso caso dos respiradores, na minha opinião.

Outros comentários estão na linha de criar um "fast track", que eu entendo como sendo alguma maneira de "encurtar caminho" naquele processo todo do fluxograma [no comentário anterior deste issue](https://github.com/Inspire-Poli-USP/Inspire-OpenLung/issues/14#issuecomment-609779681).

buenow, 2020-04-06:
Pessoal, o fast track diz respeito a produto já aprovado no exterior, pela FDA, Ag Européia, Japonesa ou Chinesa. Neste caso a aprovação será imediata se o projeto tiver alguma dessas aprovações externas. Por outro lado, o prazo da ANVISA foi reduzido para apreciação desse tipo de produto, em caso de projeto local. Creio ainda que sendo a USP esse processo tenha alguma prioridade junto à ANVISA. A imprensa informa que já existe um contato estabelecido para tal finalidade entre a USP e a ANVISA. Isso procede? Como podemos ajudar?

OttoHeringer, 2020-04-06:
Entendi. Pensei que fast track pudesse significar mais coisas além disso que você mencionou.

Sim, já existe uma conversa com alguns profs e a ANVISA. Apesar de possivelmente o tempo de apreciação ser menor, ainda é uma lista enorme de testes e exigências como as que mostrei antes.

O problema é que além dos testes do protótipo, é preciso pedir autorização para o LOCAL de fabricação (o começo do fluxograma que mostrei antes).

ArturGasparetto, 2020-04-07:
Olá pessoal, de que forma podemos contribuir com esta parte regulatória?
Eu consegui algumas das normas citadas acima pelo site da ABNT e gostaria de saber se tem algum local já definido de onde compartilhar estas normas.

xultz, 2020-04-07:
Recebi um doc contendo uma lista de normas que a ABNT está disponibilizando gratuitamente, quase metade delas se referem a ventiladores (de alguma forma), o arquivo pode ser baixado aqui:
https://gofile.io/?c=RAMekj
(Desculpe ser um arquivo .doc, mas foi o que recebi, se alguém tiver dificuldade eu converto para um formato mais acessível)

guiriole, 2020-04-07:
Boa tarde pessoal,
Sou da Riole (www.riole.com.br). Vamos começar a contribuir no desenvolvimento e possível fabricação. Eu vou tratar das questões burocráticas e estou tentando me inteirar.
Mas pelo que estudei até aqui a fabricação esta dispensada de qualquer autorização conforme a RDC nº356 de 23/03/2020.(http://portal.anvisa.gov.br/documents/10181/5809525/RDC_356_2020_.pdf/0655c7ae-8c47-4be9-bf0d-4c7b8df03e4e). 
Na mesma RDC já se estabelece alguns requisitos do produto (art. 7º).

ArturGasparetto, 2020-04-07:
Só para entender...a RDC 356 trata de EPIs e também de válvulas, circuitos e conexões respiratórias que serão usadas no ventilador?
Se for isso, então acho que a RDC 356 tem que ser usada em conjunto com a RDC 349 19/03/2020, certo?

guimoro, 2020-04-07:
> Só para entender...a RDC 356 trata de EPIs e também de válvulas, circuitos e conexões respiratórias que serão usadas no ventilador?
> Se for isso, então acho que a RDC 356 tem que ser usada em conjunto com a RDC 349 19/03/2020, certo?

Me parece que sim.

ArturGasparetto, 2020-04-07:
É, foi meu entendimento também.
Como forma de ajudar, vou pesquisar e estudar para tentar entender a legislação, normas, etc que envolvem o processo regulatório e de cadastramento, avaliação de conformidade e liberação para uso do ventilador.
Me disponho aqui a ficar em contato com quem mais estiver ajudando nesta área que é bem ampla e cheia de detalhes.

ArturGasparetto, 2020-04-07:
Estou usando como base para esse estudo de todo processo regulatório, o documento "Manual para regularização de equipamentos médicos na Anvisa" emitido em Abril de 2020.
[Manual para regularização de equipamentos médicos na Anvisa.pdf](https://github.com/Inspire-Poli-USP/Inspire-OpenLung/files/4447091/Manual.para.regularizacao.de.equipamentos.medicos.na.Anvisa.pdf)

OttoHeringer, 2020-04-07:
@ArturGasparetto obrigado por se disponibilizar em compartilhar as normas. Elas não são pagas? Se depositarmos esses pdfs por aqui não poderia "dar ruim" pra gente? Mas se tiver um link com elas, acho que não teria problema.
@guiriole, eu tinha lido essa portaria mas só caiu a ficha disso com o seu comentário, rs. Tem razão, as indústrias estão dispensadas.

Pensei numa maneira de organizar a ajuda que acho que ia ajudar MUITO: ler as normas e "filtrar" delas todos os requisitos técnicos necessários. Até agora ninguém de fato teve "coragem" de enfrentar esse "calhamaço" de normas.
Podem ir postando direto aqui mesmo, posts soltos. Depois eu junto bonitinho - ou algum de vcs pode juntar tbm e mandar um pull-request, se fizerem questão.

Aí transformaríamos essa discussão e os pontos numa página da wiki desse repositório, onde outros poderão se interar dessa questão rapidamente.

Eu queria já ter feito isso, mas me faltou tempo. Podem ajudar nisso!?

ArturGasparetto, 2020-04-07:
Oi @OttoHeringer , as normas que obtive foram apenas as que estavam disponíveis gratuitamente pelo site abntcatalogo.com.br . Contudo, considerando o que você disse sobre a possibilidade de dar algum problema, posso sim tentar disponibilizar os links aqui de forma a facilitar que cada um baixe esses documentos. Mas lembrando que algumas normas não consegui baixar pois eram pagas mesmo.
Se for de concordância e acharem necessário também, posso colocar alguns outros documentos normativos como INs, RDCs, etc que considero relevante no processo de credenciamento, certificação e liberação de uso do dispositivo, de forma a tentar centralizar toda documentação aqui.
Eu tenho mais 2 colegas de trabalho que estão estudando essas normas também, tentando entender tudo que envolve o funcionamento deste tipo de dispositivo e mapear os requisitos técnicos baseando-se nessa pilha de normas.

ArturGasparetto, 2020-04-08:
Adicionei os links do site do catálogo da ABNT para as normas que foram listadas pelo @OttoHeringer . Todas essas normas encontram-se como gratuitas no momento.

1. ABNT NBR IEC 60601-1:2010 - Equipamento eletromédico - Parte 1: Requisitos gerais para segurança básica e desempenho essencial [https://www.abntcatalogo.com.br/norma.aspx?ID=80437](url)

2. ABNT NBR IEC 60601-1:2010  Emenda 1:2016 - Equipamento eletromédico - Parte 1: Requisitos gerais para segurança básica e desempenho essencial [https://www.abntcatalogo.com.br/norma.aspx?ID=355495](url)

3. ABNT NBR IEC 60601-1-2:2017 - Equipamento eletromédico - Parte 1-2: Requisitos gerais para segurança básica e desempenho essencial - Norma Colateral: Perturbações eletromagnéticas - Requisitos e ensaios [https://www.abntcatalogo.com.br/norma.aspx?ID=383029](url)

4. ABNT NBR IEC 60601-1-6:2011 Versão Corrigida 2013 - Equipamento eletromédico - Parte 1-6: Requisitos gerais para segurança básica e desempenho essencial - Norma colateral: Usabilidade [https://www.abntcatalogo.com.br/norma.aspx?ID=307130](url)

5. ABNT NBR IEC 60601-1-8:2014 Versão Corrigida 2015 - Equipamento eletromédico - Parte 1-8: Requisitos gerais para segurança básica e desempenho essencial - Norma colateral: Requisitos gerais, ensaios e diretrizes para sistemas de alarme em equipamentos eletromédicos e sistemas eletromédicos [https://www.abntcatalogo.com.br/norma.aspx?ID=348135](url)

6. ABNT NBR IEC 60601-1-10:2010  Versão Corrigida 2013 - Equipamento eletromédico - Parte 1-10: Requisitos gerais para segurança básica e desempenho essencial - Norma colateral: Requisitos para o desenvolvimento de controladores fisiológicos em malha fechada [https://www.abntcatalogo.com.br/norma.aspx?ID=307136](url)

7. ABNT NBR IEC 60601-1-10:2010 Emenda 1:2017 - Equipamento eletromédico - Parte 1-10: Requisitos gerais para segurança básica e desempenho essencial — Norma colateral: Requisitos para o desenvolvimento de controladores fisiológicos em malha fechada [https://www.abntcatalogo.com.br/norma.aspx?ID=371257](url)

8. ABNT NBR ISO 80601-2-12:2014 - Equipamento eletromédico - Parte 2-12: Requisitos particulares para a segurança básica e o desempenho essencial de ventiladores para cuidados críticos [https://www.abntcatalogo.com.br/norma.aspx?ID=326196](url)

Obs.: _As normas técnicas listadas acima foram aprovadas pela Instrução Normativa do Ministério da Saúde nº 49 de 27 de Novembro de 2019 ([IN 49 Ministério da Saúde-NOVEMBRO DE 2019.pdf](https://github.com/Inspire-Poli-USP/Inspire-OpenLung/files/4447684/IN.49.Ministerio.da.Saude-NOVEMBRO.DE.2019.pdf)), cujos parâmetros devem ser adotados para a certificação de conformidade, no âmbito do Sistema Brasileiro de Avaliação da Conformidade (SBAC), dos equipamentos sob regime de Vigilância Sanitária._

9. ABNT NBR ISO 14971:2009 - Produtos para a saúde — Aplicação de gerenciamento de risco a produtos para a saúde [https://www.abntcatalogo.com.br/norma.aspx?ID=55540](url)

10. ABNT NBR ISO TR 24971:2014 - Produtos para a saúde - Orientações para a aplicação da ABNT NBR ISO 14971 [https://www.abntcatalogo.com.br/norma.aspx?ID=325424](url)
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

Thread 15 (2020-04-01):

Inspire-Poli-USP/Inspire-OpenLung #15: Especificação do motor

karlaycosta, 2020-04-01:
Olá pessoal gostaria de saber sobre a especificação do motor de passo, observei que nos testes https://github.com/Inspire-Poli-USP/Inspire-OpenLung/blob/master/Teste_Poli_USP_LEB_26_03_2020 a especificação está descrito 20kg e na atualização do dia "24 de Março: Modelagem 3D e testes do Protótipo V3: agora projetado para motor NEMA 23 de 15kg de torque" esta descrito com 15kg, seria um NEMA 23 de 15kg ou 20kg de torque?

emersonmoretto, 2020-04-01:
Opa, o de 15 é suficiente

Usamos o de 20 também porque é o que tínhamos em mais quantidade

Vou atualizar no git, valeuu
*Emerson Moretto*
emerson@moretto.eng.br
11 99484-0571

alberiolima, 2020-04-02:
Segundo a imagem, num ciclo de 3 segundos, a inspiração, etapa 1 do ciclo, deve levar 1 segundo.
Mas calculando com um curso de 100mm (10cm), usando um motor de passo, com 200 passos por revolução, em usar micropassos é claro, com uma barra roscada com passo 2mm. Teríamos 100passos por mm. Para percorrer 100mm são necessários 10.000passos. Então a velocidade seria de 10.000passos/segundo. E a biblioteca que controla o motor tem a informação que velocidada acima de 1.000 não é confiável, imagina 10.000

[image]

HPparanhos, 2020-04-02:
@alberiolima É quase impossível replicar esse projeto com fuso de passo 2mm. Estamos utilizando aqui um de 25mm e @emersonmoretto um de 15mm. Com isso o avanço do sistema se torna ideal com poucos passos e o motor. Esqueça neste caso de usar micropassos! Isso reduz ainda mais o torque do motor.

alberiolima, 2020-04-02:
> @alberiolima É quase impossível replicar esse projeto com fuso de passo 2mm. Estamos utilizando aqui um de 25mm e @emersonmoretto um de 15mm. Com isso o avanço do sistema se torna ideal com poucos passos e o motor. Esqueça neste caso de usar micropassos! Isso reduz ainda mais o torque do motor.

Ótimo então! Quanto a aceleração acredito que não tem necessidade, para controlar o fluxo/vazão só seria necessário ter uma tabela ou equação que retorne o valor de ml para cada posição no curso!

alberiolima, 2020-04-02:
@HPparanhos, o @emersonmoretto falou que está testando uma versão que usa PID, mas não entendi a necessidade! Você também está testando?!

HPparanhos, 2020-04-02:
PID servirá para controle da curva de respiração. Mas existem algumas dificuldades em atingir essa curva usando sistema pid, pois após "overshoot" ele continuará fazendo auto compensação com leitura dos sensores, o que pode trazer valores diferentes do esperado. Estamos em busca também de outro tipo de controle para que essa curva seja respeitada. 

Nosso foco está na validação de IHM e controle das válvulas no momento, nosso FORK já está atualizado com ultimas modificações.

andreribeiroeco, 2020-04-03:
Olá pessoal, no projeto (estou analisando a V5) tem uma peça que parece uma arruela de acrílico, que serve de guia para a peça móvel. Na pasta de cortes 2D não tem o DXF dela, aí vem a pergunta. Ela realmente é uma peça cortada em acrílico e esqueceram de gerar o DXF dela ou ela é outra peça e como está tudo a mesma cor eu me confundi? Obrigado.

karlaycosta, 2020-04-03:
Fiquei com essa dúvida também, parece que a peca foi impressa em 3D? Estou pensando em adaptar usando micro rolamento com flange tipo **F624zz**, levando em consideração a resistência e durabilidade do rolamento, creio que o @emersonmoretto possa tirar essa dúvida quanto ao material usado na peça que parece uma bucha para ajudar a deslizar a parte móvel deslocada pelo motor, o problema em usar o rolamento citado, seria na dificuldade em encontrar nas lojas!

alberiolima, 2020-04-04:
> PID servirá para controle da curva de respiração. Mas existem algumas dificuldades em atingir essa curva usando sistema pid, pois após "overshoot" ele continuará fazendo auto compensação com leitura [...]

Quais válvulas?

emersonmoretto, 2020-04-04:
> Olá pessoal, no projeto (estou analisando a V5) tem uma peça que parece uma arruela de acrílico, que serve de guia para a peça móvel. Na pasta de cortes 2D não tem o DXF dela, aí vem a pergunta. Ela [...]

é uma peça cortada a laser de PTFE, de 25mm de diametro e furo de 3mm. Mas ainda estamos avaliando se ela realmente resolve a questão do movimento linear. Está há 2 dias rodando sem parar aqui e até agora parece bom, porém há muito desgaste já. Provavelmente tenhamos que mudar pra algum material mais resistente.

alberiolima, 2020-04-11:
Fiz um código para teste de motor de passo, usando a biblioteca accelStepper, apesar de não recomendar, ela é visivelmete simples! 
https://youtu.be/Z4LCoNhKEyM 
[image]

Gustavomurta, 2020-04-18:
Srs, já divulguei no grupo do Telegram.
Estamos fusando a Biblioteca **FlexyStepper**. No meu ponto de vista, tem recursos mais avançados do que a AccelStepper. 
O controle dos movimentos são fantásticos e precisos! Defino a distancia percorrida em mm, velocidade (mm/seg) , aceleração (mm/seg2).  E enquanto o motor gira, posso testar algumas variáveis. 
https://github.com/Stan-Reifel/FlexyStepper

https://github.com/tiagocriaar/AMBU-SOL-AR/blob/master/C%C3%B3digos%20Arduino/SW_RESPIRADOR_SOL_AR_V1_40a.ino
Obs - o código esta bagunçado pois outro colega esta implementando outras funções. E estamos fazendo tudo às pressas. 

Gustavo Murta 
Anbu Sol e Ar

Gustavomurta, 2020-04-18:
Meus cálculos de RPM, usando fuso de 25 mm. 

[image]

alberiolima, 2020-04-18:
> Srs, já divulguei no grupo do Telegram.
> Estamos usando a Biblioteca **FlexyStepper**. No meu ponto de vista, tem recursos mais avançados do que a antiga AccelStepper.
> O controle dos movimentos são fantásticos e precisos! Defino a distancia percorrida em mm, velocidade (mm/seg) , aceleração (mm/seg2). E enquanto o motor gira, posso testar algumas variáveis.
> https://github.com/Stan-Reifel/FlexyStepper
> 
> https://github.com/tiagocriaar/AMBU-SOL-AR/blob/master/C%C3%B3digos%20Arduino/SW_RESPIRADOR_SOL_AR_V1_40a.ino
> Obs - o código esta bagunçado pois outro colega esta implementando outras funções. E estamos fazendo tudo às pressas.
> 
> Gustavo Murta
> Ambu Sol e Ar

> Srs, já divulguei no grupo do Telegram.
> Estamos usando a Biblioteca **FlexyStepper**. No meu ponto de vista, tem recursos mais avançados do que a antiga AccelStepper.
> O controle dos movimentos são fantásticos e precisos! Defino a distancia percorrida em mm, velocidade (mm/seg) , aceleração (mm/seg2). E enquanto o motor gira, posso testar algumas variáveis.
> https://github.com/Stan-Reifel/FlexyStepper
> 
> https://github.com/tiagocriaar/AMBU-SOL-AR/blob/master/C%C3%B3digos%20Arduino/SW_RESPIRADOR_SOL_AR_V1_40a.ino
> Obs - o código esta bagunçado pois outro colega esta implementando outras funções. E estamos fazendo tudo às pressas.
> 
> Gustavo Murta
> Ambu Sol e Ar

Mas como a maneira de controle de passos é a mesma da AccelStepper, continua o problema de não poder executar nada enquando o motor se move, e sabemos que é necessário ler sensores e efetuar cálculos. Isso pode ser resolveido com RTOS, PWM, deixar o controle do motor num processador diferente!

Gustavomurta, 2020-04-18:
Opa!!! "continua o problema de não poder executar nada enquando o motor se move"
Isso não precede! Veja o meu comentário:

E enquanto o motor gira, posso testar algumas variáveis.

alberiolima, 2020-04-18:
> Opa!!! "continua o problema de não poder executar nada enquando o motor se move"
> Isso não precede! Veja o meu comentário:
> 
> E enquanto o motor gira, posso testar algumas variáveis.
> 
> https://github.com/Stan-Reifel/FlexyStepper/tree/master/examples/Example7_MovingWhileDoingOtherThingsToo

Coloque calculo com variaveis float ou double

Gustavomurta, 2020-04-18:
A minha ideia é usar o tempo de delay do Plato, para fazer isso... 
Não testei ainda. O que acha ?

Gustavomurta, 2020-04-18:
Concordo que é um desafio, mas estou confiante que conseguirei.

alberiolima, 2020-04-18:
> Concordo que é um desafio, mas estou confiante que conseguirei.

Uma *gambiarra seria executar "stepper.processMovement();" numa interrupção por tempo

alberiolima, 2020-04-18:
Uma solução +/- seria separar o controle do motor do restante do sistema, já que isso é crítico!
poderia fazer comunicação entre os módulos usando SPI que é uma comunicação muito rápida, já tem implementada no hardware da muitos microcontroladores!

Gustavomurta, 2020-04-19:
Alberio, muito obrigado pelas dicas! 
Se o Arduino não aguentar, não hesitarei em sugerir mudança para o ESP32.
Dois processadores rodando 10 vezes o clock de um Arduino. (até 240 MHz)

alberiolima, 2020-04-19:
> Alberio, muito obrigado pelas dicas!
> Se o Arduino não aguentar, não hesitarei em sugerir mudança para o ESP32.
> Dois processadores rodando 10 vezes o clock de um Arduino. (até 240 MHz)

Acho que um STM32F103 já resolveria, com 20Kb de RAM, e 64Kb ou 128Kb de flash com clock de 72mhz, acredito que já seria suficiente, pode continuar usando a IDE do Arduino. Usando FreeRTOS. (bluepill)
Evitaria o ESP32 pelo ADC ser um pouco ruim de usar, e pelo fato de a maioria dos módulos prontos ter antena de RF, isso talez seja um problema para validar! Com certeza você teria um grande porder de processamento, muita RAM e muita FLASH, mais que o necessário!

Tyrtech, 2020-05-03:
Já fizeram testes de longa duração? eu uso esses motores a muito tempo em maquinas cnc, e eles queimam se forem usados por um longo período, os meus já queimaram com 4 horas de uso, ai coloquei um cooler atrás que resolveu o problema, nunca testei com dissipador de calor, vocês estão pensando em um método de resfriamento pro motor ou não tiveram problemas?

Gustavomurta, 2020-05-04:
Tyrtech, 
Se o motor da sua CNC, esta queimando depois de 4 horas de uso, é porque tem algum problema na sua CNC. Ou você esta sobrecarregando os motores além do que eles suportam. Ou pode até ser que seja baixa qualidade do motor (chinês). Use marcas de boa qualidade e sugiro que reclame com o  fabricante da sua CNC. 
Eu trabalhei por muitos e muitos anos com manutenção de impressoras de grande porte, que usavam motores de passo gigantes (que puxavam os formulários). Essas impressoras IBM eram usadas o dia inteiro e dentro desse período de muitos anos, troquei uma vez o motor!!
Os motores de passo são super resistentes, e além do mais, os drivers atuais tem proteção contra sobre-corrente!

Gustavomurta, 2020-05-04:
Se alguém se interessar, criei esse Tutorial no Lab de Garagem, da montagem de um Sensor Hall para medições do RPM do motor do eixo sem fim do nosso Ambu Sol e Ar. Usando rotor de motor sem escovas BLDC, poderá fazer medições precisas dos movimentos do Respirador. Registrando todos os pulsos com um analisador lógico, poderá fazer aferições precisas de tempo de inspiração, tempo de platô e tempo de expiração. 
http://labdegaragem.com/forum/topics/sensor-hall-de-rota-o-rpm

Nessa imagem, consta os pulsos do motor durante o Tempo de inspiração, e os pulsos do motor para retorno do motor. 
 
[image]

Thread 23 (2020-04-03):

Inspire-Poli-USP/Inspire-OpenLung #23: Especificação do sensor de pressão

m-rodrigues-souza, 2020-04-03:
Qual sensor de pressão está sendo utilizado nos testes? Tem o part number?

OttoHeringer, 2020-04-03:
Oi Matheus.
Boa pergunta. Nesse momento, para fazer os testes do algoritmo de controle, estamos medindo a pressão com equipamentos "padrão" que se usam associados a pulmões mecânicos, como esse, por exemplo:
[image]

Se você conseguir uma maneira confiável de fazer sensoriamento de pressão, acho que já "tá valendo" pra fazer os testes de controle.

Agora, o componente em si de controle, o @emersonmoretto estava pensando em usar um muito comum usado em carros.

Vou ver aqui e atualizo esse issue.

Mas se você quiser, tbm pode sugerir um sensor. Lembre-se que ele tem que ser barato e acessível "a pronta entrega", e em "qualquer lugar".

karlaycosta, 2020-04-03:
No momento estou utilizando o GYBMEP (pressão, temperatura e umidade) para testes aqui, um sensor muito confiável, porém, ainda estou analisando como acoplar ao sistema de mangueiras junto ao ambu.
Link com a descrição: [https://produto.mercadolivre.com.br/MLB-1200500296-gy-bme280-saia-temperatura-sensor-umidade-de-alto-exatido-_JM?quantity=1](url)

alberiolima, 2020-04-03:
> No momento estou utilizando o GYBMEP (pressão, temperatura e umidade) para testes aqui, um sensor muito confiável, porém, ainda estou analisando como acoplar ao sistema de mangueiras junto ao ambu. [...]

Conheço bem os sensores BMP085, BMP180,BMP280 e BME280. Uso para calculo de velocidade vertical e altitude, são bem confiáveis.
Mas seu range deve ser levando em consideração: 300hPa a 1100hPa. Pois a pressão atmosférica ao nível do mar é 1013,25hPa.
O range útil, para o fim, seria 1013,25hPa a 1100hPa, resultando 86,75hPa que corresponde a 88,46cmH2O. Mas no III Consenso Brasileiro de Ventilação Mecânica, Tabela 1, diz que a pressão máxima inspiratória é de 80 a 120cmH2O. Isso não seria um problema?

alberiolima, 2020-04-03:
Para usar sensor que não seja diferencial é necessário ler a pressão antes de iniciar a operação, para usar como referência, só que a pressão atmosférica é dinâmica ela muda durante o dia por vários motivos. Será que isso também não seria ruim? Acredito que seja necessário usar um sensor diferencial ou dois sensores.

karlaycosta, 2020-04-03:
Vou olhar o datasheet, se não estou enganado podemos alterar o valor de referência da pressão atmosférica (1013,25hPa) para fazer a calibração do sensor, assim poderíamos atingir o range (80 a 120cmH2O) com folga. Lembando que o sensor ficaria confinado dentro de uma válvula com o ambu, assim não levaria em consideração a pressão atmosférica e sim a pressão da tubulação, mas ainda estou analisando essa adaptação e como faria o confinamento do sensor, @alberiolima obrigado pelo feedback, estou olhando um sensor diferencial para comprar pois até a adaptação do sensor é mais fácil.
Link com a descrição: [https://www.usinainfo.com.br/sensor-de-pressao-arduino/sensor-de-pressao-diferencial-mpx5700dp-0kpa-a-700kpa-3812.html](url)

alberiolima, 2020-04-03:
> Vou olhar o datasheet, se não estou enganado podemos alterar o valor de referência da pressão atmosférica (1013,25hPa) para fazer a calibração do sensor, assim poderíamos atingir o range (80 a [...]

Separei dois modelos para analisar melhor:  (acredito que precisaremos de pressão negativa,também)
Sensor proximo do ideal XGZP6847040KPGPN -40KPa a 40KPa (-408cmH2O a 408cmH2O)
  XGZP6847020KPG (0 a 20Kpa)

buenow, 2020-04-05:
Pessoal, caso ainda não tenho decidido o sensor de pressão, seria o caso de considerarmos essa proposta?
[lps27hhw_sensor_pressao.pdf](https://github.com/Inspire-Poli-USP/Inspire-OpenLung/files/4434926/lps27hhw_sensor_pressao.pdf)

buenow, 2020-04-05:
Esta é uma proposta de uso possível...
[Presure measure.docx](https://github.com/Inspire-Poli-USP/Inspire-OpenLung/files/4434930/Presure.measure.docx)

alberiolima, 2020-04-05:
> Esta é uma proposta de uso possível...
> [Presure measure.docx](https://github.com/Inspire-Poli-USP/Inspire-OpenLung/files/4434930/Presure.measure.docx)

Muito bom, eu estava procurando um projeto assim que vi no passado, quando pesquisar sobre sensores de velocidade de vento, até tendei replicar, mas acabei usando esse:
https://www.banggood.com/3pcs-Digital-Barometric-40KPa-Pressure-Sensor-Module-Liquid-Water-Level-Controller-Board-p-1590571.html?cur_warehouse=CN

alberiolima, 2020-04-05:
Vou tentar montar uma câmara de vacuo para calibrar os sensores! Tenho alguns modelos, que uso em altímetros barométricos.
[image]

VitorFrost, 2020-04-06:
Como a pressão com certeza não será igual em todo o sistema, talvez seja necessário nessa primeira etapa colocar o sensor tanto na entrada (ambu) e outro no final (paciente). Fazer um levantamento de perda de pressão. O que vai alterar a pressão no sistema: altura entre o paciente e o ambu, VÁLVULAS, FILTROS, conectores, curvas das mangueiras, etc. Ou seja, tudo. Em um equipamento "tradicional" aonde é feita a leitura de pressão?
A pergunta mais importante! Na etapa de validação pela Anvisa, como os equipamentos são validados? O que é acoplado? Eles testam com os filtros HME ou HEPA? Assim como esse projeto sofrerá perdas, os equipamentos consagrados também sofrem e eu suspeito que ele mostra uma leitura nas condições ideais do teste, mas que no uso há uma pequena imprecisão.

OttoHeringer, 2020-04-14:
https://github.com/Inspire-Poli-USP/Inspire-OpenLung/issues/43#issuecomment-612534274

@danilochui encontoru uma referência de outro sensor da BOSCH que poderia ser usado

Gustavomurta, 2020-04-18:
Alguém já fez testes com esse sensor ? Comprei um hoje pelo ML. 
Mp3v5010dp 
https://www.nxp.com/docs/en/data-sheet/MP3V5010.pdf
0 to 10 kPa (0 to 1.45 psi)
0.1 to 3.1 V Output 

Gustavo Murta 
Ambu Sol e Ar

alberiolima, 2020-04-18:
> Alguém já fez testes com esse sensor ? Comprei um hoje pelo ML.
> Mp3v5010dp
> https://www.nxp.com/docs/en/data-sheet/MP3V5010.pdf
> 0 to 10 kPa (0 to 1.45 psi) ou (0 a 101,972 cm H2O)
> 0.1 to 3.1 V Output
> 
> Application Examples
> • Hospital Beds
> • HVAC
> • Respiratory Systems
> • Process Control
> 
> Gustavo Murta
> Ambu Sol e Ar

Nunca usei esse aí, mas usei alguns parecidos, resolução de 12bits, e comunicação SPI, boa resolução com ótima velocidade de comunicação! O próprio sensor já tendo um ADC já melhora muita coisa! Acredito que será uma boa opção!

alberiolima, 2020-04-18:
> Alguém já fez testes com esse sensor ? Comprei um hoje pelo ML.
> Mp3v5010dp
> https://www.nxp.com/docs/en/data-sheet/MP3V5010.pdf
> 0 to 10 kPa (0 to 1.45 psi) ou (0 a 101,972 cm H2O)
> 0.1 to 3.1 V [...]

Coloca o link do mercadolivre

Gustavomurta, 2020-04-19:
Alberio, acho que existe alguma restrição sobre colocar links comerciais aqui. 
Pesquise por Mp3v5010dp no ML. 
Corrigindo : 
A saída desse sensor é um sinal analógico - 0 a 3,1V .
Ele não tem um ADC interno. Seria ótimo se tivesse.

alberiolima, 2020-04-19:
> Alberio, acho que existe alguma restrição sobre colocar links comerciais aqui.
> Pesquise por Mp3v5010dp no ML.
> A saída desse sensor é um sinal analógico - 0 a 3,1V .
> Ele não tem um ADC interno. Seria ótimo se tivesse.
> Vi que o módulo que indicou tem um ADC de 12 bits. Muito bom.

Que pena pelo ADC, estava pensando no módulo pronto.

VitorFrost, 2020-04-23:
Esse projeto pode ser útil: https://hackaday.io/project/170622-visp-ventilator-inline-sensor-package

alexaquino, 2020-04-23:
Pessoal, a uma empresa nacional que pode produzir o sensor dentro do range necessário (faixa de 0 - 60CmH2O e saída indo de 4 a 20mA). Ele já nos forneceu um para um projeto e poderia nos fornecer algumas amostras para testes no Inspire. Caso haja interesse posso colocar ele em contato com o @OttoHeringer pra ele realizar o envio.

[Manual NP400.pdf](https://github.com/Inspire-Poli-USP/Inspire-OpenLung/files/4522630/manual_np400_v10x_d_portugues.pdf)

[image]

VitorFrost, 2020-04-23:
@alexaquino Muito bom conseguir um fornecedor nacional!
Verifiquei que no datasheet que o sensor funciona com 12V e mede-se a corrente de saída. O fabricante deu algum circuito básico de leitura? Uma simples ponte de Wheatstone é suficiente? Necessita de um AmpOp pra trabalhar com 5V?
Obrigado!

Gustavomurta, 2020-04-24:
Faço parte da equipe Ambu Sol e Ar, que esta fazendo testes com o sensor acima - NP400 modificado. 
NP-400 - modificado
INPUT - 0 - 60 cmH2O
OUTPUT - 4 - 20mA

Um colega nosso, o Felipe Jonathan, fez algumas medições, usando o circuito que desenhei para ele, seguindo as orientações do engenheiro do fabricante. Como é um sensor analógico industrial, usamos um resistor em série para medir a tensão. Existem módulos específicos para fazer isso, mas não temos em mãos. 
https://www.itead.cc/wiki/4-20mA_Sensor_Brick
Não fizemos aferições de medições ainda, para comprova-las. 

Esse é o diagrama:
[image]

Gustavomurta, 2020-04-28:
Pesquisando documentos da NXP, encontrei mais um sensor muito interessante!  MPXV5004
https://www.nxp.com/docs/en/data-sheet/MPXV5004G.pdf

-  0 to 3.92 kPa, Differential and Gauge (39,97 cm H2O) 

- 1.5% maximum error for 0 to 100 mm H2O

- Alimentação  5,0 V

- Sensitivity - 1 V / KPa  (10,197 cm H2O)

Gustavomurta, 2020-04-28:
**Como calibrar um sensor de 40 cm H20.** 
Eu não sabia que era tão simples!

A melhor calibração deve ser feita em duas partes. Uma pressão deverá ser  medida a 0 mm de H2O e a outra  quando a tubulação estiver a 40 cm de H2O. A diferença nas contagens de ADC divididas por 40 cm fornecerá o número de contagens de ADC (tensão)  por cm. 

Referência : Altitude Pressure EXperimental (APEX) Sensor Board
[https://www.nxp.com/docs/en/application-note/AN3956.pdf](url)

[image]

Samu-vaz, 2020-05-21:
Senhores,
Tenho trabalhado com os sensores da série MPX5700, e está funcionando bem!
Ele faz o trabalho de pressão diferencial e, através de um BMP(E)280, monitoro as alterações de pressão Atmosférica no ambiente, e com um algoritmo bastante simples eh possível fazer a compensação no sistema através dos dados de ambos sensores.
O BME280 nos ajuda ainda na questão de umidade relativa...
Estou trabalhando sensores em redundância:
- Um BMP280 com o BME280 para a variável Pressão Atmosférica;
- Um HTU21D com o BME280 para a variável Umidade Relativa.
Nos 3 sensores monitoro a temperatura também.
Estou bastante satisfeito com o resultado. Caso alguém esteja trabalhando de maneira similar, seria ótimo falar a respeito, trocar experiências e até mesmo aprimorar esse sistema.

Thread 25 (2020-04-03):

Inspire-Poli-USP/Inspire-OpenLung #25: Arruela de teflon

OttoHeringer, 2020-04-03:
Olá pessoal, no projeto (estou analisando a V5) tem uma peça que parece uma arruela de acrílico, que serve de guia para a peça móvel. Na pasta de cortes 2D não tem o DXF dela, aí vem a pergunta. Ela realmente é uma peça cortada em acrílico e esqueceram de gerar o DXF dela ou ela é outra peça e como está tudo a mesma cor eu me confundi? Obrigado.

_Originally posted by @andreribeiroeco in https://github.com/Inspire-Poli-USP/Inspire-OpenLung/issues/15#issuecomment-608226320_

OttoHeringer, 2020-04-03:
Boa observação.
Essa peça é uma "arruela de teflon". Fizemos ela pegando um tarugo cilíndrico de 10 mm de diâmetro e cortando fatias de 5mm numa serra circular. Essas fatias foram colocadas na cortadora a laser e cortadas no tamanho certo.
Usar uma arruela de teflon foi uma dica do HPparanhos que recebemos já faz mais de uma semana, então créditos a ele!

OttoHeringer, 2020-04-03:
Vamos atualizar e colocar esse arquivo faltante.

andreribeiroeco, 2020-04-03:
> Vamos atualizar e colocar esse arquivo faltante.

Boa, aí eu já pego o DXF pra cortar aqui. Obrigado.

closed 2020-04-26 by breno-helf

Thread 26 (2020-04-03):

Inspire-Poli-USP/Inspire-OpenLung #26: Algoritmo de Controle por PID

OttoHeringer, 2020-04-03:
PID servirá para controle da curva de respiração. Mas existem algumas dificuldades em atingir essa curva usando sistema pid, pois após "overshoot" ele continuará fazendo auto compensação com leitura dos sensores, o que pode trazer valores diferentes do esperado. Estamos em busca também de outro tipo de controle para que essa curva seja respeitada. 

Nosso foco está na validação de IHM e controle das válvulas no momento, nosso FORK já está atualizado com ultimas modificações.

_Originally posted by @HPparanhos in https://github.com/Inspire-Poli-USP/Inspire-OpenLung/issues/15#issuecomment-607877154_

OttoHeringer, 2020-04-03:
Ainda na tentativa de abordagem por PID, estamos testando o código [desse repositório](https://github.com/eduoda/odamv).

alberiolima, 2020-04-03:
> PID servirá para controle da curva de respiração. Mas existem algumas dificuldades em atingir essa curva usando sistema pid, pois após "overshoot" ele continuará fazendo auto compensação com leitura dos sensores, o que pode trazer valores diferentes do esperado. Estamos em busca também de outro tipo de controle para que essa curva seja respeitada.
> 
> Nosso foco está na validação de IHM e controle das válvulas no momento, nosso FORK já está atualizado com ultimas modificações.
> 
> _Originally posted by @HPparanhos in [#15 (comment)](https://github.com/Inspire-Poli-USP/Inspire-OpenLung/issues/15#issuecomment-607877154)_

@OttoHeringer, PID para controlar a pressão através de uma válvula, ou o volume?
Quantas e quais são as valvulas que precisam ser controladas?

marcusvscosta, 2020-04-04:
Olá, conheci o seu projeto pela midia e pela internet. Sou professor de controle e automação e trabalho em desenvolvimento e estudo de estratégias de controle. Poderia contar mais em como é modelado o sistema do controle do respirador? Modelo matemático ou métodos de identificação? Tem os pontos de dados para fazer identificação do modelo?  Desde já agradeço a atenção!

OttoHeringer, 2020-04-06:
Oi @alberiolima, eu criei [uma documentação](https://github.com/Inspire-Poli-USP/Inspire-OpenLung/wiki/Entenda-o-Problema) que talvez explique melhor essa questão.

@marcusvscosta obrigado por se disponibilizar.
O andamento do algoritmo de controle está desatualizado aqui no repositório. Isso será atualizado em breve.
Mas eu já posso adiantar por aqui o que está rolando:
- O controle PID não funciona bem para esse problema. Erramos em considerá-lo em primeiro lugar como estratégia de controle.
- Estamos usando uma outra abordagem muito interessante, que é modelar o sistema como um tradicional circuito oscilatório RC, em que a resistência é a resistividade das vias aéreas e a "capacitância" é a chamada complacência do pulmão. A "corrente" é o fluxo de ar. A estratégia é "medir" R e C durante os ciclos de respiração e inspiração para ajustar automaticamente a equação de fluxo de ar para os níveis desejados pelo operador.
  - Uma outra coisa legal disso é que vamos poder fornecer ao operador valores de resistividade das vias aéreas e a complacência do pulmão, que são muito importantes para fazer diagnósticos da situação do paciente "ao vivo".

OttoHeringer, 2020-04-06:
Esse final de semana parece que o algoritmo ando MUITO bem. Vou ver se consigo fazer o Felipe Fava, que é quem está programando isso, pode subir o código aqui no GitHub. Ele está fazendo no MatLab.

marcusvscosta, 2020-04-06:
Se modelar como um sistema RC, um PI já resolve, pois o PID o termo derivativo torna o sistema mais lento, dificultando a chegada ao setpoint de referencia. Trabalho com matlab. Precisa levar também o problema do tempo de amostragem na implementação. Uma forma usual de dimensionar o tempo amostragem é considerar como ao menos 1/10 da constante de tempo dominante do sistema. Tempo de amostragem muito pq gera aliasing (aparecimento de ruidos indesejáveis) e tempo de amostragem grande desobedece o teorema de Nyquist.

alberiolima, 2020-04-06:
> Esse final de semana parece que o algoritmo ando MUITO bem. Vou ver se consigo fazer o Felipe Fava, que é quem está programando isso, pode subir o código aqui no GitHub. Ele está fazendo no MatLab.

OK, eu acredito que possa ajudar com o código! Já que conheço tanto mecânica, quanto programação!

OttoHeringer, 2020-04-06:
Pessoal, criamos outro repositório com o código. Ainda preciso documentar, mas quem entender de controle e saber que estamos usando um modelo de circuito RC para o sistema talvez consiga entender.

Junto com o código, tem uma pasta com todos os dados de caracterização do sistema usando vários testes que viemos fazendo.

https://github.com/Inspire-Poli-USP/Inspire-OpenLung-RCModelFirmware

Quando documentar, coloco aqui.

Esse novo repositório virará um submódulo desde.

alberiolima, 2020-04-06:
Eu vejo um sistema com 3 partes, IHM, Operacional, Sensores/Alarmes. 
Sensores e Alarmes assim como o Operacional são tarefas críticas e acredito que deve ser feitas em processadores diferentes, um conversando com o outro. 
Sensores -> IHM, para mostrar valores/alarme na tela
Sensors -> Operacional, para passar do modo mandatório para assistido (por interrupção)
IHM -> Operacional, para configurações e iniciar/parar
(Sensores também seria capaz de detectar a operação, saber em que ponto está da respiração, e monitorar seu funcionamento correto, e passaria a informação para o IHM) 
Opcionalmente, quando em operação não teria comunicação partindo do Operacional

d-oliveira, 2020-04-07:
> Pessoal, criamos outro repositório com o código. Ainda preciso documentar, mas quem entender de controle e saber que estamos usando um modelo de circuito RC para o sistema talvez consiga entender. [...]

O link está correto?

OttoHeringer, 2020-04-07:
@d-oliveira , tivemos problemas envolvendo a política de disponibilização desse código. Estou pensando como resolver isso.  Se você entrar no [grupo do Telegram](https://t.me/openlungpoliusp) e me procurar por lá, posso falar pessoalmente com vc sobre isso.

Desculpa aí pessoal, resolvendo uns problemas aqui!

sandrompassos, 2020-04-07:
Olá, Pessoal... Sou do aluno de Engenharia de Controle e Automação do IFMS campus Três Lagoas... Estou montando com professores um grupo de estudos na área de Engenharia Clínica... Estamos acompanhando esse projeto e devemos montar um protótipo para testes... Esperamos poder colaborar de alguma forma... Parabéns pela iniciativa...

OttoHeringer, 2020-04-08:
Oi @sandrompassos , me manda uma mensagem no telegram!? Talvez possamos ajudar mandando um protótipo pronto pra vcs irem testando; ainda estamos decidindo para quem vamos mandar uns protótipos, mas um critério é mandar para grupos de ensino e pesquisa.

OttoHeringer, 2020-04-08:
Pessoal, estava conversando com o @emersonmoretto e acho que seria legal organizar as informações sobre os algoritmos de controle que já são usados nos respiradores profissionais; quem puder ajudar, por favor dê uma olhada num novo Issue sobre isso.

juliosouzabrsp, 2020-04-08:
Boa tarde pessoal, sou o Julio Cesar e estive interagindo no grupo do Telegram. O algoritmo de controle dos fabricantes envolvem muitos detalhes e blocos relativos ao controle em si e outros dedicados as condições de contorno ou para acionar alarmes da maneira mais inteligente possível digamos e dentro dos critérios estabelecidos nas normativas vigentes

juliosouzabrsp, 2020-04-08:
Uma prática que vi funcionar nesses casos é instrumentar o protótipo com o máximo de sensores possíveis e ler simultaneamente todos os sinais nos diferentes pontos do sistema, e subsistemas. Estando com os sensores indicando valores razoáveis em todos os pontos, fica mais fácil realizar observações que juntamente com a modelagem teórica devem indicar os parâmetros de controle necessários para estabilidade mínima necessária para segurança do paciente.

juliosouzabrsp, 2020-04-08:
O compartimento interno do sistema de ventilação é dividido em duas partes. O compartimento de entrada ou admissão de oxigênio, que no início do ciclo absorve o gás do cilindro de O2, até que o valor de pressão interna do compartimento seja suficiente para fechar a válvula de admissão e abrir o compartimento de saída/ linha do paciente. Ao transmitir a pressão do O2 para o pulmão do Paciente, se faz o uso de um ciclador controlado, desta forma, o mecanismo faz aumentar a pressão na linha do paciente até o necessário para preencher o pulmão com O2 via traquéias de borracha. Quando o pulmão recebe o volume de ar necessário e pressão, o ciclador fecha o compartimento de saída e o pulmão + caixa torácica, expulsam o CO2 para o ambiente. Nesse momento é preciso ter controle da pressão de saída de CO2 do pulmão para que não fique abaixo da pressão natural do corpo, que mantém o pulmão inflado. Essa é a pressão chamada PEEP.

juliosouzabrsp, 2020-04-08:
Cada compartimento vai sofrer influências que podem ser medidas ou simuladas por blocos para identificação das variáveis mais influentes e refinamento dos controles

juliosouzabrsp, 2020-04-08:
Os modos de falha de qualquer uma das malha de controle e do sistema não podem resultar em situação que possa causar dano parcial ou permanente ao paciente.

juliosouzabrsp, 2020-04-08:
Os controles e atuadores precisam estar configurados de maneira que em caso de falha de algum componente crítico o sistema seja capaz de interromper o funcionamento e acionar um alarme ou entrar em mode de auto recuperação, para garantir a segurança básica e desempenho essencial deste equipamento de suporte a vida

alberiolima, 2020-04-08:
[image]

breno-helf, 2020-04-26:
Esse issue pode ser re-aberto em momento oportuno.

closed 2020-04-26 by breno-helf

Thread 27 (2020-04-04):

Inspire-Poli-USP/Inspire-OpenLung #27: Vídeo e divulgação

juloko, 2020-04-04:
Primeiramente parabéns pelo projeto.

No entanto está faltando vídeo e divulgação do projeto. O projeto alcançará um determinado nível de sucesso quando pessoas leigas na área conhecerem ele e se interessarem, motivará os engenheiros e técnicos ao redor para produzirem...

Um vídeo bobo para rolar no whatsapp já serve (minha visão).

breno-helf, 2020-04-04:
Acho também que outras coisas na parte de divulgação poderiam ser feitas, como criar uma página web (poderia ser no proprio github mesmo, com o github pages) colocando milestones do projeto com fotos e vídeos (com os dados ficaria bem tranquilo organizar isso).

breno-helf, 2020-04-15:
Oba, sei que vocês já apareceram na mídia e tudo, mas ainda existe interesse nisso? Poderia ajudar também. Acredito que se não houver interesse melhor fechar a issue.

breno-helf, 2020-04-20:
Oi @juloko !

Acabei de achar um vídeo bacana que poderia rodar no whatsapp, como você sugeriu. https://youtu.be/hkaXHtFTmG4 , isso aqui serve?

Nesse caso vou fechar essa Issue e abrir outra mais relativa a uma página de divulgação que faremos mais adiante.

juloko, 2020-04-22:
Perfect! Parabéns! Vou baixar e divulgar.

juloko, 2020-04-23:
@breno-helf gostaria de contribuir com a página de divulgação.

breno-helf, 2020-04-23:
Tranquilo @juloko , estou pensando em abrir um github pages daqui uns dias, te mantenho atualizado!

breno-helf, 2020-04-30:
Vou reabrir esse Issue pois acredito que podemos fazer um github pages legal com a documentação que temos no repositório e na wiki.

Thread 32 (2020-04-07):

Inspire-Poli-USP/Inspire-OpenLung #32: Esquematização do Sistema Completo

OttoHeringer, 2020-04-07:
Eu vejo um sistema com 3 partes, IHM, Operacional, Sensores/Alarmes. 
Sensores e Alarmes assim como o Operacional são tarefas críticas e acredito que deve ser feitas em processadores diferentes, um conversando com o outro. 
Sensores -> IHM, para mostrar valores/alarme na tela
Sensors -> Operacional, para passar do modo mandatório para assistido (por interrupção)
IHM -> Operacional, para configurações e iniciar/parar
(Sensores também seria capaz de detectar a operação, saber em que ponto está da respiração, e monitorar seu funcionamento correto, e passaria a informação para o IHM) 
Opcionalmente, quando em operação não teria comunicação partindo do Operacional

_Originally posted by @alberiolima in https://github.com/Inspire-Poli-USP/Inspire-OpenLung/issues/26#issuecomment-610095253_

OttoHeringer, 2020-04-07:
Obrigado por sumarizar esses pontos, @alberiolima.
Acho importante fazer isso para também apontar áreas onde há menos esforços ainda.

Você poderia fazer um diagrama sobre isso? Muita gente está pedindo algo do tipo para entender melhor o contexto de onde o projeto sendo documentado nesse repositório se encaixa.

alberiolima, 2020-04-08:
Fiz um rascunho rápido! De como eu acredito que seria a base inicial. 
[image]

alberiolima, 2020-04-08:
[image]

AlvaroAguiar, 2020-04-14:
Teremos uma visão explodida do projeto? Isso facilita para o leigo que porventura queira produzir o equipamento (meu caso). Cada parte com o nome da peça e o link para o corte a laser (sugestão).

breno-helf, 2020-04-15:
Oi @alberiolima , você se importaria de submeter um Pull request com essas esquematizações? Podemos iterar sobre elas e tornar em uma contribuição técnica para o projeto!

Obrigado!

alberiolima, 2020-04-16:
> Oi @alberiolima , você se importaria de submeter um Pull request com essas esquematizações? Podemos iterar sobre elas e tornar em uma contribuição técnica para o projeto!
> 
> Obrigado!

Olá @breno-helf , não entendi, o que exatamente quer que faça? Qualquer coisa me envia um e-mail, tem no meu perfil do github. Abraço

breno-helf, 2020-04-20:
Oi @alberiolima !

Vou mandar um email com essa mesma mensagem, mas acredito que seu esquema que você compartilhou nessa Issue poderia entrar no repositório do projeto. Para isso seria nescessário um Pull Request para incluir elas. Tem uma explicação no repositório de como fazer isso (https://github.com/Inspire-Poli-USP/Inspire-OpenLung/blob/master/CONTRIBUTING.md#como-fazer-as-contribui%C3%A7%C3%B5es). Colocando esse seu esquema como contribuição, além de você entrar como um dos contribuidores do projeto, sua contribuição passa a ser uma contribuição técnica que vai ser usada por outras pessoas desenvolvendo o respirador!

Qualquer dúvida sobre como fazer um pull request, ou caso você não possa fazer, me avise! Eu posso fazer o Pull Request por você se você quiser (Mas nesse caso infelizmente seu nome não fica como de contribuidor). 

Abraços!

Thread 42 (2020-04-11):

Inspire-Poli-USP/Inspire-OpenLung #42: Volume do Ambu

lfelipev, 2020-04-11:
Boa noite a todos!

Gostaria de saber qual o volume do Ambu da versão atual do projeto, é uma dúvida que tenho sobre o volume do Ambu ser suficiente para manter uma pressão constante no intervalo de tempo T2 da curva característica.

alberiolima, 2020-04-11:
> Boa noite a todos!
> 
> Gostaria de saber qual o volume do Ambu da versão atual do projeto, é uma dúvida que tenho sobre o volume do Ambu ser suficiente para manter uma pressão constante no intervalo de tempo T2 da curva característica.

A curva é apenas o gráfico do comportamento do sistema respiratório, a expiração ela acontece naturalmente, a pressão vai diminuindo porque o ar vai saindo do sistema, você precisa apenas fechar a válvula quando chegar na pressão PEEP. Se o dispositivo já tiver uma válvula de PEEP, você precisa apenas aguardar o final do tempo T2 para iniciar uma nova inspiração.
_(informação confirmada com médico)_

alberiolima, 2020-04-11:
> Boa noite a todos!
> 
> Gostaria de saber qual o volume do Ambu da versão atual do projeto, é uma dúvida que tenho sobre o volume do Ambu ser suficiente para manter uma pressão constante no intervalo de tempo T2 da curva característica.
Observando o grafico, o fluxo de ar é constante em INSP (T1), sai de zero vai direto para o valor expecífico, a pressão em T1, representa a resistência que o sistema repiratório do paciente oferece ao fluxo. Volume representa a quantidade de ar que entrou. Em T2, pressão representa a força que o sistema respiratório faz para empurrar o ar para fora.

[image]

OttoHeringer, 2020-04-14:
Oi @lfelipev,

boa pergunta, isso não está especificado no nosso BOM na página inicial. Vou colocar lá.

Usamos um Ambu com capacidade de 1600 mL. E sim, estamos conseguindo "entregar" o necessário.

@alberiolima , excelente comentário, vou referenciá-lo na documentação do "Entendendo o Problema".

OttoHeringer, 2020-04-14:
Atualização da documentação sobre respiração linkando esse Issue feita aqui:
https://github.com/Inspire-Poli-USP/Inspire-OpenLung/wiki/Entenda-o-Problema#vari%C3%A1veis-de-cada-paciente
Lista de materiais (BOM) atualizada aqui:
https://github.com/Inspire-Poli-USP/Inspire-OpenLung#partes-m%C3%A9dicas

closed 2020-04-14 by OttoHeringer

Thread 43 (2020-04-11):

Inspire-Poli-USP/Inspire-OpenLung #43: Desafio: Válvula PEEP

OttoHeringer, 2020-04-11:
Oi pessoal!

Temos um desafio para quem quer ajudar com soluções de hardware: desenvolver uma válvula PEEP.

Informações específicas sobre isso estão documentadas [nessa página da wiki](https://github.com/Inspire-Poli-USP/Inspire-OpenLung/wiki/Desafio:-V%C3%A1lvula-PEEP).

Conforme descrito no link anterior, vamos discutir e compartilhar conteúdos por aqui!

danilochui, 2020-04-11:
Boa noite. Vi que na página da descrição do desafio, é sugerido que se use sensores automotivos. Fazendo uma pesquisa rápida aqui, me deparei com esse vídeo no Youtube. O rapaz lê um sensor MAP automotivo com Arduíno. Aqui: https://www.youtube.com/watch?v=83LuzJTIbAw
Dá para ver que ele mede a pressão ambiente como 1000,XX mBar. Os valores depois da vírgula já possuem uma incerteza de uns 0,5 mBar. Como 1 cmH2O é 0,98 mBar, então temos uma incerteza de aproximadamente 0,5 cmH2O. 
Lá na página fala: "Ter precisão nos valores configurados - ou seja, por exemplo: selecionar uma pressão de 7 cmH2O deve manter uma medida de pressão real de 7 cmH20"
Na verdade, usando um MAP automotivo, teríamos 7 +- 0,5 cmH2O. Isso é aceitável?

adalmirabdala, 2020-04-13:
Princípio: Uso de VENTILADOR como regulador de PRESSÃO.
Boa noite. Segue uma alternativa de válvula PEEP, evitando: a)mola (fadiga), b)válvulas c)obstrução na ocorrência de falha. Tem controle preciso no PWM do arduino, na escala requerida. Também utilizei o BME280 no arduino para aferir as medidas práticas encontradas.
No protótipo utilizei um ventilador 12vcc de secador de cabelo + "adaptação" para cano com escala, como segue em foto. Esse ventilador não tem a capacidade requerida, mas o princípio foi demonstrado.
Princípio: usar ventilação forçada na saída da traqueia (expiração), no sentido de criar contrapressão constante no sistema, que pode ser vencida pelo paciente sem restrição.
Medição de pressão positiva: 3,4mmH2O (medição utilizando BME280, BMP280 >>955,0-951,7 hPa)
Teste prático: montagem do sistema com saída para baixo em copo de água, observado entre 3 e 3.5 cm o vencimento da coluna de água e formação de bolhas.
Problemas: ruído, a contrapressão soma com a pressão do ambu.
Obs.: O BME280 tem 2 endereços, podendo ter um segundo redundante em outro ponto.
[image]
[image]

adalmirabdala, 2020-04-13:
obs: deve ter mais uma válvula unidirecional para evitar risco de reinalação.

adalmirabdala, 2020-04-13:
Valvula PEEP utilizando a própria coluna dágua como válvula.
Segue abaixo esboço de sistema utilizando a própria coluna dágua como agente pressurizador do sistema de expiração + válvula unidirecional. Ainda não montei um protótipo, porém é o mais simples que consegui.
Desvantagem: regulagem manual e dificuldade de estanqueidade do sistema.
[image]

danilochui, 2020-04-13:
Colocando duas válvulas solenoides uma de entrada de água e outra de saída e uma bóia, é possível fazer essa regulagem manual virar eletrônica.

OttoHeringer, 2020-04-14:
@adalmirabdala suas ideias são muito criativas. A mais interessante das duas é o controle por nível de água, e o @danilochui complementou bem sobre como controlar isso eletronicamente. Essa ideia é elegante porque além de ser um pouco mais simples que a do ventilador, ela "resolve" um problema que tem no ventilador: contaminação. Alguns projetos de ventiladores emergenciais inclusive estão propondo usar essa "armadilha de água" no final com a finalidade principal de ajudar evitar contaminar o ar ambiente com o que passou pelo paciente e vice-versa - porque em tese, boa parte do que viria junto com o ar expirado ficaria na água.

O que estamos procurando é algo mais na linha do que o @danilochui estava pesquisando: um componente pronto que originalmente é usado para uma finalidade mas que resolveria quase que perfeitamente nosso problema.

OttoHeringer, 2020-04-14:
Aproveitando, vejam o que o @emersonmoretto estava trabalhando no final de semana:
https://youtu.be/Lm-YNxPOsxA

É uma proposta simples, mas que ainda está sendo testada aqui. Não queríamos depender dela porque claramente é mais complexa do que pegar um componente "pronto" e adaptá-lo.

Pensando bem aqui, o que precisamos, no fundo, é: uma "torneira" que a gente consiga ficar controlando o quanto abrimos e fechamos através de um arduino, por exemplo.

felipeosi, 2020-04-14:
Tem uma solução comercial para controle de boost em carros turbo de corrida.  Usa bico injetor de carro, que suporta infinitos (quase) ciclos de fechamento e abertura, e o tempo morto de abertura tá na ordem de 0,80 milisegundos pra 12 volts no acionamento.

https://produto.mercadolivre.com.br/MLB-1220289052-suporte-bicos-para-booster-eletronico-integrado-injeco-_JM?matt_tool=86155663&matt_word&gclid=CjwKCAjwvtX0BRAFEiwAGWJyZJ_YDjBeiw1HFAIqMFFgC_jmCoKLNmMKpJqoB8pvnZefIgZnXFpCVBoCrXgQAvD_BwE&quantity=1

1 bico controla o envio do gas pressurizado para o volume de controle, e o outro a liberação do gás para atmosfera. No caso do ventilador, talvez usar só um bico injetor liberando o gás do volume de controle para atmosfera seja suficiente. Mas se não, tem a opção de colocar o outro bico captando ar do zona pressurizada do ambu, e enviando para o volume de controle.

emersonmoretto, 2020-04-15:
> oço de sistema utilizando a própria coluna dágua como agente pressurizador do sistema de expiração + válvula unidirecional. Ainda não montei um protótipo, porém é o mais simples que consegui.

é então, esse era o jeito que usavam na década de 80 né. Mas parece que não se pode mais usar desse jeito por questões de contaminação e tem um problema de excesso de bolhas que faz com que ela não funcione bem (quando em peep alto, solta tanta bolha que afeta o mecanismo de pressao da água e nessa situação ele falha e acaba segurando pra baixo o valor)

emersonmoretto, 2020-04-15:
> a: "Ter precisão nos valores configurados - ou seja, por exemplo: selecionar uma pressão de 7 cmH2O deve manter uma medida de pressão real de 7 c

Olha, pra fins do algoritmo de controle essa resolução não ajuda muito, na verdade acaba proporcionando um erro de fitting de curva considerável. A gente tá usando um sensor com resolução de 44 mV/cm H2O pra ficar legal. ex: mpx5010

emersonmoretto, 2020-04-15:
> Tem uma solução comercial para controle de boost em carros turbo de corrida. Usa bico injetor de carro, que suporta infinitos (quase) ciclos de fechamento e abertura, e o tempo morto de abertura tá [...]

Infelizmente bico injetor automotivo não dá... 1) ele tem resistencia muito grande (acima de 15), essa resistencia causaria um enorme atraso na saída fazendo o paciente não exalar o ar totalmente, o que por consequencia, aumentaria MUITO o CO2 no corpo, 2 minutos com vazão prejudicada o paciente já pode ter dano; e 2) vazão, um bico injetor tem uma vazão de alguns mL/min só, a expiração chega a ter 600ml em pouco mais de 1 segundo

emersonmoretto, 2020-04-15:
> Princípio: Uso de VENTILADOR como regulador de PRESSÃO.
> Boa noite. Segue uma alternativa de válvula PEEP, evitando: a)mola (fadiga), b)válvulas c)obstrução na ocorrência de falha. Tem controle [...]

Muito criativa a ideia, mas acho que isso não segura em situações extremas como em 15 cm h2o.
Teria que ser um sistema muito vedado e um ventilador muito forte.

VitorFrost, 2020-04-15:
O maior problema dos ventiladores é conseguir o produto rápido. Poderia utilizar-se de dois ventiladores em série, para uma pressão maior. 
Só que isso vai gerar um barulho no estilo de aspirador de pó, vai atrapalhar muito em ambiente hospitalar e elevar o stress de todos. Não podemos deixar isso de lado.

VitorFrost, 2020-04-15:
A minha grande dúvida é, vocês sabem aonde está ocorrendo a falha da válvula Peep? É a mola que entra em fadiga? Ou é a borracha de vedação?
Se for a borracha, não é ressecamento da mesma?

VitorFrost, 2020-04-15:
O mais fácil e seguro seria automatizar a válvula Peep mecânica já existente por meio de um servomotor

OttoHeringer, 2020-04-16:
> A minha grande dúvida é, vocês sabem aonde está ocorrendo a falha da válvula Peep? É a mola que entra em fadiga? Ou é a borracha de vedação?
> Se for a borracha, não é ressecamento da mesma?

ATUALIZAÇÃO

Desenvolvemos uma solução seguindo essa ideia que o @VitorFrost deu!

Ainda não ficou perfeita porque o hardware precisa ser melhor; em breve divulgaremos a documentação.

Mais informações na [página atualizada da wiki](https://github.com/Inspire-Poli-USP/Inspire-OpenLung/wiki/Ajuda-da-Comunidade-com-a-V%C3%A1lvula-PEEP) sobre esse asunto.

VitorFrost, 2020-04-16:
@emersonmoretto 
Eu pensei numa melhoria nesse sistema que vocês pensaram. Nesse modo aqui, o ajuste é feito com 1/4 de volta apenas, dando velocidade na resposta, e aumentando as frações de pressão disponíveis.
E eu fiz no papel na verdade metade da válvula, o ideal é ela ser espelhada no eixo, ficando duas janelas opostas e a parte móvel em formato quase de um 8.
[image]
[image]

filzek, 2020-04-16:
A esterilização da saída poderia ser por uma micro tela energizada com íons,  de maneira que passe por uma UV, ozônio, estes micro disparos eletrônicos poderiam formar um esterilizador de passagem,

felipeosi, 2020-04-16:
> A esterilização da saída poderia ser por uma micro tela energizada com íons, de maneira que passe por uma UV, ozônio, estes micro disparos eletrônicos poderiam formar um esterilizador de passagem,

Tem filtros HEPA que já são usados nos aparelhos comerciais e são super baratos. Pode melhorar a filtragem com mais esses recursos, sem dúvida

felipeosi, 2020-04-16:
[https://grabcad.com/library/valvula-peep-pra-respirador-pulmonar-mecanico-1](url)

Esse design vai a valvula de prioridade automotiva e um atuador linear. Usar um solenoide pode ser uma opção, mas não estou seguro quanto a capacidade de vedação com solenoide. Pq precisa ter uma pressão na sede da valvula pra vedar.

[image]

lmsrv, 2020-04-17:
Pesquisando em relação às válvulas PEEP, desde o início achei a ideia da válvula Boehringer a mais fácil de ser replicada e com maior confiabilidade.

Ela funciona baseada no peso de esferas, que são erguidas de acordo com a pressão de expiração do paciente.

Dessa maneira, apresenta uma resposta constante ao longo do tempo e não depende de molas, imãs, motores, etc.

Os maiores inconvenientes são:

•	Ela tem que operar na vertical.
•	O ajuste tem que ser manual.

Desenhei um modelo semelhante, que trabalharia com pequenas “arruelas”. Essas “arruelas” acrescentariam peso conjunto, regulando o sistema em intervalos de 1 cmH2O.

Seria interessante enviar 02 conjuntos com as “arruelas” (peças 02 e 03) com o aparelho. Uma seria estaria sendo utilizada e segunda serviria para fazer os ajustes se for necessário fazer a troca.

Para trocar, basta retirar a tampa e inserir o novo conjunto em questão de segundos.

[image]
[image]
[image]
[image]

Gustavomurta, 2020-04-18:
Boa tarde, estou vendo que estão tentando usar válvulas mecânicas. 
Por que não usar um sensor eletrônico de pressão? Existe alguma limitação em usá-lo?

1) MPX5010 - 0 a 101,97 cmH2O
https://www.nxp.com/docs/en/data-sheet/MPX5010.pdf
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

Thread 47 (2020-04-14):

Inspire-Poli-USP/Inspire-OpenLung #47: Manual de Montagem

OttoHeringer, 2020-04-14:
Obrigado pela sugestão. O melhor mesmo seria um manual de montagem. Aliás, isso é um ótimo novo Issue.

_Originally posted by @OttoHeringer in https://github.com/Inspire-Poli-USP/Inspire-OpenLung/issues/46#issuecomment-613487881_

Eu vi que o manual do fork do @HPparanhos está bem legal.
https://github.com/HPparanhos/CITI-OpenLung/blob/master/Manual%20de%20montagem/564135%20(1).pdf

Alguém teria uma sugestão a mais?

AlvaroAguiar, 2020-04-14:
> Obrigado pela sugestão. O melhor mesmo seria um manual de montagem. Aliás, isso é um ótimo novo Issue.
> 
> _Originally posted by @OttoHeringer in [#46 (comment)](https://github.com/Inspire-Poli-USP/Inspire-OpenLung/issues/46#issuecomment-613487881)_
> 
> Eu vi que o manual do fork do @HPparanhos está bem legal.
> https://github.com/HPparanhos/CITI-OpenLung/blob/master/Manual%20de%20montagem/564135%20(1).pdf
> 
> Alguém teria uma sugestão a mais?

Otto, Boa tarde. Talvez minhas expectativas tnham sido errôneas. Andei vendo a parte burocrática de poder certificar o equipamento junto a ANVISA etc, e me parece que somente indústrias poderão ser habilitadas para a produção dos respiradores. Corrija-me, por favor, caso esteja errado. Minha expectativa era de poder fazer eu próprio (sou engenheiro mecânico e conheço uma coisinha ou outra), através de vaquinha ou outro processo de crow funding, a compra de peças e manufaturar algumas unidades para minha cidade, ajudar como fosse possível... Se obtivesse algum dinheiro de prefeituras próximas, talvez até produzir para essas pequenas cidades também. Moro em Tupã - SP, cuja população tem cerca de 60.000 habitantes. Não há indústrias capacitadas por aqui, só boa vontade mesmo (mas logo-logo teremos mortes). Por isso fiz a sugestão da visão explodida pra o equipamento, o que ajudaria (no velho sistema Lego) pessoas não técnicas a montar o respirador. Outra sugestão que faço, depois de todo esse preâmbulo, é um passo-a-passo de como inserir o firmware (aí talvez um entendedor de Arduino seja necessário). Um turorial, do início ao fim seria a perfeição para isso tudo, com locais explícitos pra o download dos softwares. Mas o tempo urge. Temos pouco tempo disponível. Talvez em duas semanas já estejamos iniciando o colapso do sistema público de saúde. Ponho-me à disposição para ajudar.

rafae2k, 2020-04-26:
@OttoHeringer Proponho a criação de uma animação (video) do processo de montagem, passo a passo, detalhando os pormenores do processo de montagem. Em um segundo momento podemos criar uma video aula acompanhando a instalação do firmware. Por último, podemos criar uma página nos moldes do [Ifixit.com](url) como este [https://pt.ifixit.com/Device/iPhone_11_Pro](url) ou nos moldes dos manuais da Prusa 3D [https://help.prusa3d.com/en/category/original-prusa-i3-mk3s-kit-assembly_280](url)

Cheguei agora na página do projeto e gostaria de saber se posso iniciar esta primeira ideia da criação da animação do processo de montagem ou se algo do gênero já está sendo realizado.

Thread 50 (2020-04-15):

Inspire-Poli-USP/Inspire-OpenLung #50: readme.md Driver do motor DW322E

gdmpg, 2020-04-15:
# A que parte do projeto esse Issue se refere?

- [ ] Software
- [ ] Hardware
- [ ] Dados
- [X] Documentação
- [ ] Outro

### Reportando um erro

No setor de Partes Eletrônicas, consta 1x Driver DW322E da Leadshine após não encontra-lo verifiquei no side da empresa e encontrei o modelo DM322E  como pode ser visto em 

`http://www.leadshine.com/productdetail.aspx?type=products&category=stepper-products&producttype=stepper-drives&subtype=general-stepper-drives&series=dm&model=dm322e`

### Sugestão de melhoria

Verificar se realmente é uma versão diferente DW ou se é só um erro de escrita.

breno-helf, 2020-04-20:
Oi @gdmpg , muito obrigado pela Issue! Acredito que seja de fato uma versão diferente, mas acredito que o @OttoHeringer ou o @VitorFrost podem confirmar isso melhor.

Se for o caso você conseguiria fazer um Pull Request sugerindo essa mudança? 

Obrigado!

VitorFrost, 2020-04-27:
Infelizmente não sei responder, precisamos de alguém interno ao projeto para responder e confirmar.
MAS, no fork do CITI consta o modelo que mencionou!
https://github.com/HPparanhos/CITI-OpenLung

weverton-rosa, 2020-04-27:
Procurei também pelo modelo DW mas um dos fornecedores me retornou dizendo que desconhece essa versão e me orçou o modelo DM.

VitorFrost, 2020-05-01:
Pelos vídeos de divulgação, o driver já foi trocado por um outro de 24V. 
Pelas imagens, e por ser 24, deve ser o DM-542:
[image]
Fonte: https://www.youtube.com/watch?v=kMW-kKYsIrE

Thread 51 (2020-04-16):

Inspire-Poli-USP/Inspire-OpenLung #51: Sensor de fluxo preciso e de baixo custo

drelp7, 2020-04-16:
# A que parte do projeto esse Issue se refere?

- [ ] Software
- [ X ] Hardware
- [ ] Dados
- [ ] Documentação
- [ ] Outro

Olá Pessoal. É possível desenvolver um sensor de fluxo de baixo custo e que consiga medir com resolução de 1 L/min. Para isso é necessário utilizar uma placa de orifício utilizada em baixas vazões e  pequenos diâmetros (norma ASME MFC-14M). Fiz algumas simulações teóricas aqui, e para conseguir uma resolução de 1 L/min é necessário ter um sensor que meça diferencial com resolução de 25 mmH2O (o MPX5010DP acredito que consiga isso). Digo isso, porque é importante que o respirador tenha o modo VCV no combate ao Covid, e para tanto é necessário medir e controlar o fluxo. No modelo por ambu, o fluxo pode ser facilmente controlado pela velocidade do motor durante a inspiração.

Fiz um protótipo aqui de placa de orifício, bem simples e funcional, que pode ser impresso em 3D. Assim que tiver os testes, caso se interessarem posso postar aqui.

Link com equações baseadas na norma ASME MFC-1M:  http://excelcalculations.blogspot.com/2011/10/small-bore-gas-orifice-meter-flow.html

Segue também em anexo arquivo do excel para fazer os cálculos.

[SmallDiaGasOrificeMeterASME2001-placa.xlsx](https://github.com/Inspire-Poli-USP/Inspire-OpenLung/files/4489780/SmallDiaGasOrificeMeterASME2001-placa.xlsx)

OttoHeringer, 2020-04-21:
Muito obrigado @drelp7 ! É exatamente esse tipo de contribuição que estamos procurando.

Você conseguiria fazer um pull-request dessa informações como uma página da wiki?

drelp7, 2020-04-21:
Boa tarde. Encomendei a placa de orifício por impressora 3D, acredito que chegue amanhã. Assim que eu montar aqui e tiver algum resultado posto pra vocês em um pull-request.

closed 2020-04-21 by drelp7

guiriole, 2020-04-21:
Boa tarde,
Desculpem, mas essa notícia procede?

https://www1.folha.uol.com.br/equilibrioesaude/2020/04/ventilador-pulmonar-da-usp-ja-pode-entrar-na-linha-de-producao.shtml

VitorFrost, 2020-04-23:
> 
> 
> Boa tarde,
> Desculpem, mas essa notícia procede?
> 
> https://www1.folha.uol.com.br/equilibrioesaude/2020/04/ventilador-pulmonar-da-usp-ja-pode-entrar-na-linha-de-producao.shtml

A sua pergunta é relevante, mas ficou fora de contexto. Verifique a informação e resposta nesse issue:
https://github.com/Inspire-Poli-USP/Inspire-OpenLung/issues/49#issuecomment-617166121

JonathasKerber, 2020-04-23:
Boa tarde. Qual foi a solução definida para o problema da medição do fluxo? Estamos com esse problema nos projetos aqui em Manaus.

OttoHeringer, 2020-04-24:
Oi @JonathasKerber. No projeto ainda não tem um sensor de fluxo, mas nos testes estamos usando esses equipamentos aqui, por exemplo:
https://github.com/Inspire-Poli-USP/Inspire-OpenLung/wiki/Sistema-de-Testes

drelp7, 2020-04-24:
Olá. Então, fiz alguns testes aqui usando uma placa de orificio em um tubo com 17mm de diâmetro interno e a placa com orificio de 6mm no centro e 3mm de espessura, utilizando um sensor de pressão diferencial com resolução de 1cmH2O a resolução vai melhorando de 5 Até 1L/min entre vazões de 10 e 60L/min. Vou fazer os testes utilizando um sensor de pressão com resolução de 0,20cmH2O. E com certeza a resolução da vazão vai melhorar bastante. Conseguindo 1L/min de resolução entre 10 e 60L/min é mais que suficiente.

JonathasKerber, 2020-04-24:
> Oi @JonathasKerber. No projeto ainda não tem um sensor de fluxo, mas nos testes estamos usando esses equipamentos aqui, por exemplo:
> https://github.com/Inspire-Poli-USP/Inspire-OpenLung/wiki/Sistema-de-Testes

Então vocês estão parametrizando o OpenLung através dos testes com essa instrumentação do link?  Como que fica a realimentação do sistema? Eu vi que vocês tiveram que fechar o algoritmo de controle, o que é uma pena, mas acontece. Eu sou de um instituto de P&D de Manaus, se houverem mais informações que possam ser compartilhadas, elas são bem-vindas.

Aqui estamos calibrando com o [Neós AVM100](http://www.neos.ind.br/produto/avm100/) e partindo para o diferencial de pressão para termos as medições de fluxo, é o que está parecendo ser o mais viável no momento.

OttoHeringer, 2020-04-24:
> Então vocês estão parametrizando o OpenLung através dos testes com essa instrumentação do link? Como que fica a realimentação do sistema? Eu vi que vocês tiveram que fechar o algoritmo de controle, [...]

A realimentação pode ser feita com esses equipamentos mesmo, que usamos principalmente para testar os algoritmos de controle.

Por favor, me procure no grupo do Telegram (https://t.me/openlungpoliusp) e me mande uma mensagem em privado para que eu possa orientá-lo sobre como solicitar acesso ao projeto completo. Desculpe não poder estar disponibilizando tudo aqui.

Luizhym, 2020-05-08:
Olá. Resolveram a questão do sensor de fluxo? Caso necessário, posso ajudar, tenho experiência no assunto.

drelp7, 2020-05-08:
Olá. Consegui desenvolver aqui um sensor de pressão diferencial, mas está dando um erro alto, de +-50 ml. Todavia percebi depois que a placa de orifício estava com vazamento. Mandei imprimir outra. Mas se quiser pode comentar a sua experiência que com certeza vai ajudar.

Luizhym, 2020-05-08:
Trabalhei com o desenvolvimento de máquinas de anestesia. Tive um contato com sensores de fluxo por diferencial de pressão, limitadamente, mas entendo em linhas gerais. Quais as dificuldades que estão enfrentando com este tipo de sensor? Poderia detalhar melhor?
Trabalhei bastante com sensores de fluxo do tipo fio quente, uma opção bem interessante.
Quais os requisitos para este sensor? Estão em alguma página ou documento?

drelp7, 2020-05-08:
Então se você quiser me add no whatss te explico melhor. N°: 44999529184.

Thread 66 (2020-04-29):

Inspire-Poli-USP/Inspire-OpenLung #66: Fuso Trapezoidal

andreuch, 2020-04-29:
# A que parte do projeto esse Issue se refere?

- [ ] Software
- [x] Hardware
- [ ] Dados
- [ ] Documentação
- [ ] Outro

   Estou com extrema dificuldade em encontrar um local para comprar o fuso, na especificação do projeto. Alguém pode informar onde posso comprar os seguintes componentes:
- Acoplador de Garra Drylin E para eixo redondo de 10 mm de diâmetro
- Fuso Trapezoidal de 10 mm de diâmetro, 15 cm de comprimento e passo de 25 mm
- Castanha de Latão TR10 e passo de 2,5 mm
   O passo e a castanhas são de 2,5mm ou 25mm?

eliaspereira9, 2020-05-01:
Tive as mesmas dificuldades na construção do projeto. O passo do fuso e da castanha devem ser idênticos para que possa funcionar perfeitamente. Este fuso de passo 25 mm não é vendido comercialmente, você terá que procurar algum profissional que usine o fuso e a castanha. Na minha cidade em Ponta Grossa - PR o valor mais baixo que consegui para a usinagem das duas peças foi R$ 600, sendo que caso alguém consiga mais barato aceito ajuda também pois pago o fuso e o frete.  Quanto ao acoplador você consegue encontrar em lojas de parafusos ou ferramentas mas antes precisa ter o diâmetro do rotor do motor pois varia entre modelos.

andreuch, 2020-05-01:
Ok. Agradeço as informações.
Atenciosamente,
André

Enviado do meu iPhone

bernardes01, 2020-05-13:
Olá,

Demorei para encontrar o fuso e a castanha, só achei quando coloquei o código que estava na lista de materiais no Google. Pelo que sei, só tem uma empresa que comercializa o fuso "stand", é a IGUS, fica em Jundiaí-SP, visitei eles semana retrasada.

Porem, há um problema, a IGUS importa os materiais da Alemanha, ou seja, caso acabe o estoque, demoraria para chegar a nova remessa, teríamos que achar um fornecedor secundário também, de preferencia que fabrique aqui no Brasil...

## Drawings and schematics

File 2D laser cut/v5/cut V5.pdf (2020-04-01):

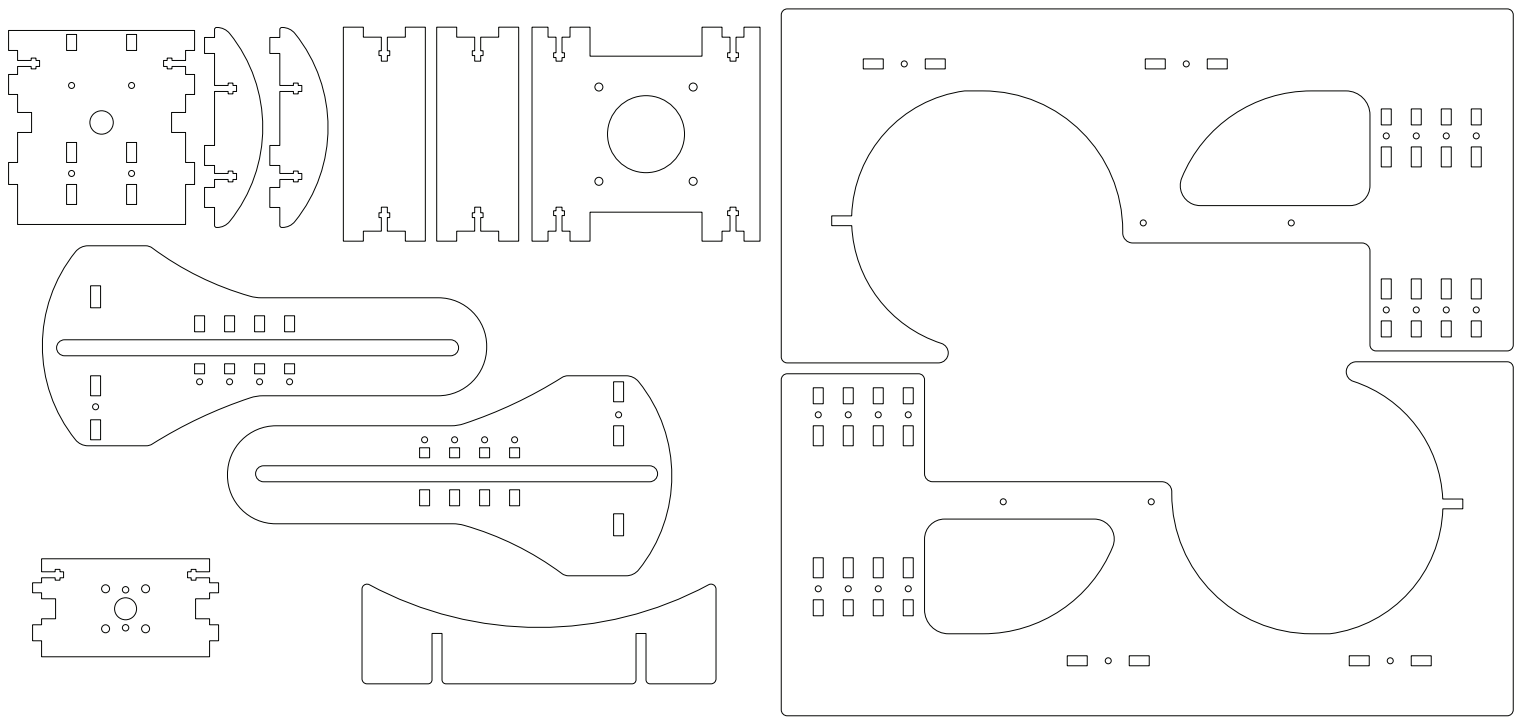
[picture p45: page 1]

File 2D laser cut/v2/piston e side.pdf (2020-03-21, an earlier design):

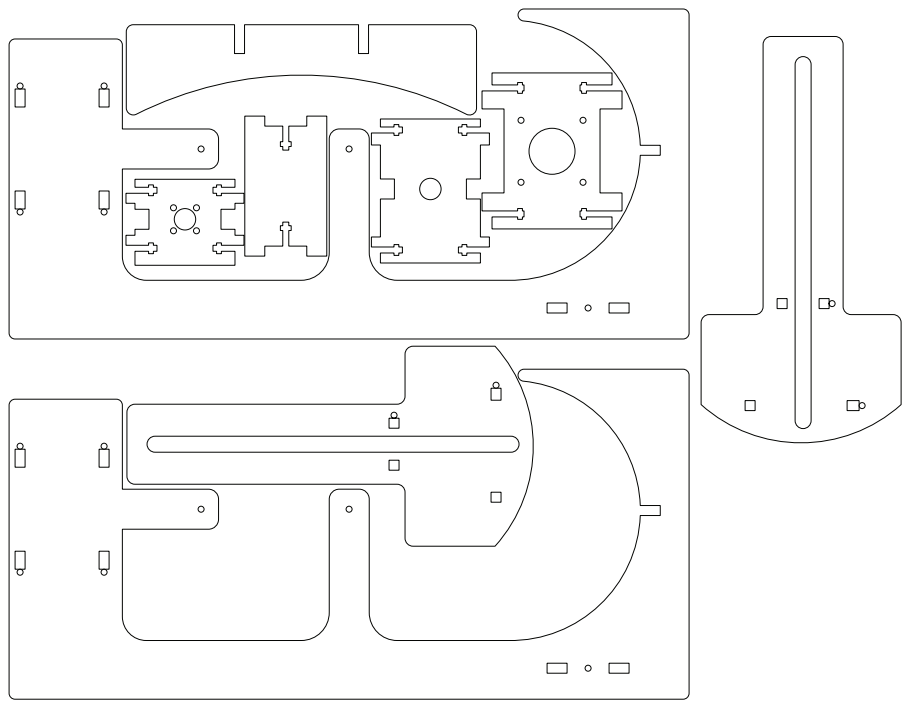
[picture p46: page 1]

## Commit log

2020-03-21 initial version
    [CITI OpenLung.f3d]
2020-03-21 2d files
    [ambu-bag support V1.dxf, nut plate V1.dxf, piston V1.dxf, piston support plate V1.dxf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]
2020-03-21 VERSAO 2
    [CITI-OpenLung V2.f3d, ambu support plate v2.dxf, base support plate v2.dxf, nut plate v2.dxf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]
2020-03-21 tava faltando uns furos
    [piston v2.dxf, side v2.dxf]
2020-03-21 arquivo de corte
2020-03-22 3d model of 2.2
    [CITI-OpenLung V2.2.f3d]
2020-03-22 pequeno ajuste na peca que suporta o ambu
    [ambu support V2.2.dxf]
2020-03-23 teste do firmware e correcoes nos cortes v2.2
    [ambu support V2.2.dxf, nut plate V2.2.dxf]
2020-03-24 V3 - adjust for nema 23 stepper
    [bag support V3.dxf, base plate V3.dxf, motor plate V3.dxf, nut plate V3.dxf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]
2020-03-25 V4!!
    Ajustes para diminuir atrito e ser mais resistente a torcao
    [ambu support V4.dxf, bottom plate V4.dxf, motor plate V4.dxf, nut plate V4.dxf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]
2020-03-25 upgrade com protocolo de comunicacao
2020-03-26 Update OpenLung-firmware.ino
    firmware do arduino que permite parametrizar os comandos para o motor de passo.
    Todos os comandos devem ser enviados via serial e cercados de < e >
    ex: <i>
2020-03-27 Readme Language Update (#3)
    * Change to Portuguese
    Translating everything to portuguese to improve local collaboration.
    * Correção nos Headings
    Arrumando tamanho dos headings e outras identações no texto.
    * Correção de bulletpoints na lista de eletrônicos
2020-03-27 Adicionando disclaimers e abordagens
    Listando disclaimers importantes para bom uso do projeto conforme orientado por membros do Inspire Poli-USP.
    Inclusão de justificativa do nosso projeto com base em nossa abordagem de desenvolvimento.
2020-03-27 Correção de erros de markdown
2020-03-27 Correção de outro erro de markdown
2020-03-27 Supressão de auto-linkagem obsoleta
    Linking para a página da organização obsoleta devido a transferência de do repositório novo
2020-03-27 Atualização dos contatos
    Supressão dos contatos do Emerson para desafogá-lo.
2020-03-27 Testes feitos na Escola Politécnica da USP no laboratório de Engenharia Biomédica (#6)
    * Add files via upload
    * Add files via upload
    * Add files via upload
    * Teste_Poli_USP_LEB_26_03_2020
2020-03-30 3D model V4.1
    Pequeno aumento de 1 mm de espaçamento entre o pistão e a estrutura.
2020-03-30 2D files for V4.1
    Arquivos para corte a laser do modelo 3D da versão 4.1
    [all pieces V4.1.dxf, ambu support V4.1.dxf, bottom plate V4.1.dxf, motor plate V4.1.dxf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]
2020-03-30 Pequena modificação na estrutura do projeto. (#7)
    * 3D model V4.1
    * 2D files for V4.1
    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
    [all pieces V4.1.dxf, ambu support V4.1.dxf, bottom plate V4.1.dxf, motor plate V4.1.dxf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]
2020-04-01 V5 2D files
    [ambu support V5.dxf, bottom plate V5.dxf, cut V5.dxf, piston V5.dxf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]
2020-04-01 update de infos para V5
2020-04-02 Criação do README da pasta de Dados Experimentais
    O README descreverá a organização da pasta Dados Experimentais
2020-04-02 Criação do README da pasta de relatórios
    O README conterá informações e links referentes a organização dos documentos da pasta de relatórios
2020-04-02 Updates finais do Código de Conduta
    Adicionando seções finais, referência e índice.
2020-04-02 Problemas de markdown arrumados
2020-04-02 Correção de erro na linkagem de seções
2020-04-02 Adição de Código de Conduta, Como Contribuir e Princípios de Design (#19)
    * Create CONTRIBUTING.md
    * Criação do README da pasta de Dados Experimentais
    * Criação do README da pasta de relatórios
    * Update CONTRIBUTING.md
    * Create CODE_OF_CONDUCT.md
    * Updates finais do Código de Conduta
    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
2020-04-02 Uploading Prototype Version 5 photo
2020-04-02 Adição de foto da versão 5 do protótipo
2020-04-02 Deleção de Foto muito grande
    Foto muito grande da versão 5 do protótipo. Outra com menor resolução será adicionada.
2020-04-02 Nova foto da versão 5 adicionada
    Agpora uma foto de tamanho ideal
2020-04-02 Link da wiki adicionado
    Wiki colocada como mais um exemplo de como contribuir com a documentação
2020-04-03 Adição de links e reestruturação
    Adição de vários links para documentos importantes do projeto e reestruturação da organização das informações
2020-04-03 CONTRIBUTING: Conserte URLs quebradas em links (#22)
    Algumas URLs estão quebradas:
    - Por uso de "##" em vez de "#"
    - Por typo ("OInspire-Poli-USP" em vez de "Inspire-Poli-USP")
    - Link da tradução de post sobre mensagens de commit está incorreto.
    Vamos corrigir esses links.
2020-04-03 Remova arquivos .DS_Store desnecessários (#10)
    Arquivos .DS_Store são criados automaticamente pelo programa Finder, do
    macOS, para armazenar atributos de pastas. Eles não têm utilidade para
    demais usuários, e poluem os diff's e diretórios do repositório.
    Portanto, remova todos os .DS_Store já incluidos e adicione um
    .gitignore que impeça futuras inclusões de tais arquivos.
2020-04-03 Update README.md
    Descrição da abordagem e princípios simplificada e link para documento de tema relacionado atualizado.
2020-04-03 Update CONTRIBUTING.md
    Link para Principios_e_abordagem.md atualizado
2020-04-03 Update README.md
    Erro de markdown corrigido
2020-04-05 Update README.md
    Descrição mais completa em "porque mais um projeto como esse" e mudança para discurso atemporal em "motivação".
2020-04-05 Create README.md
    Pasta de Imagens da Wiki criada
2020-04-05 Create Wiki_Entenda_o_Problema
    Adicionando página da wiki com explicações do problema sob o ponto de vista do controle.
2020-04-05 Update README.md
    Link para página da Wiki adicionado
2020-04-05 Update README.md
    Redundância de texto suprimida
2020-04-05 Add files via upload
    Imagens da a Página da Wiki "Sistemas de Testes" adicionadas
2020-04-05 Delete Wiki_Sistema_de_Testes_IMG6.jpg.png
    Imagem de tamanho errado deletada
2020-04-05 Add files via upload
    Upload da imagem 6 da página da wiki "Sistema de Testes" de tamanho corrigido
2020-04-06 Create Sistema_de_Testes.md
    Página sobre nosso sistema de testes criada
2020-04-06 Update Wiki_Entenda_o_Problema.md
    Informações sobre feedbacks locais de especialistas adicionada
2020-04-06 Update README.md
    Pequena edição de markdown feita
2020-04-06 Update README.md
    Link para vídeo do protótipo funcionando adicionado
2020-04-09 Update README.md
    Markup de emojis adicionado
2020-04-09 Update Wiki_HOME.md
    Email de contato atualizado
2020-04-10 Update CONTRIBUTING.md
    Informações atualizadas sobre a restrição de conteúdos do repositório
2020-04-10 Delete ambu-bag support V1.dxf
    Documento de versionamento redundante deletado
    [ambu-bag support V1.dxf]
2020-04-10 Delete nut plate V1.dxf
    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
    [nut plate V1.dxf]
2020-04-10 Delete piston V1.dxf
    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
    [piston V1.dxf]
2020-04-10 Delete piston support plate V1.dxf
    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
    [piston support plate V1.dxf]
2020-04-10 Delete side V1.dxf
    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
    [side V1.dxf]
2020-04-10 Delete stepper plate V1.dxf
    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
    [stepper plate V1.dxf]
2020-04-10 Delete acrylic cut 5mm.pdf
    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
2020-04-10 Delete acrylic cut 5mm.svg
    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
2020-04-10 Update README.md
    Desambiguação do significado de "especificações" adicionada
2020-04-10 Update README.md
    Erro de informação na BOM corrigido
2020-04-10 Update README.md
    Link para página da wiki atualizado
2020-04-10 Update README.md
    Link para lista de projetos da soptechint adicionada
2020-04-11 Create Wiki_Desafio:_Válvula_PEEP.md
    Página de desafio de construção da válvula PEEP criada
2020-04-11 Update Wiki_Desafio:_Válvula_PEEP.md
    Links para o Issue #43 adicionados
2020-04-11 Update README.md
    Link para desafio da válvula PEEP adicionada no início do README
2020-04-14 Update README.md
    Informações de partes médicas adicionadas na BOM
2020-04-14 Update Wiki_Entenda_o_Problema.md
    Informações sobre variáveis de cada paciente adicionadas
2020-04-14 Criando template para novos pull requests (#40)
2020-04-14 Criando template de issue (#39)
2020-04-16 Update README.md
    Atualização sobre o desafio, links de iniciativas da USP de combate à COVID e no andamento do projeto
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2020-04-22 Criando novos templates de issue (#59)
    * Criando novos templates de issue
    Atualizando os templates de issue para a versão mais recente
    * Delete ISSUE_TEMPLATE.md
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2020-05-14 adicionando wiki de midia (#76)
    * adicionando wiki de midia
    * fixing remark
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2020-06-05 Adicionando página de outros projetos (#87)
    * Adicionando página na wiki de outros projetos, bem como adicionando os outros projetos ao site
    * Ajustando problemas apontados pelo sistema de integração contínua e colocando link no README
2020-06-24 Melhorando o site de Documentação e adicionando referência a Caninos Loucos (#90)
    * Improving website and adding reference to Caninos Loucos
    * adding midia
    * fix remark error
